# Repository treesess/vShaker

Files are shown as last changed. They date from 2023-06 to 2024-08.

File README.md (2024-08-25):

# vShaker

low-cost shake table and demonstrative test models based on Klipper and FDM mainly for educational purposes

Please refer to the latest folder v231111. Currently there is no full build version to share but only the linear module part has been sorted and uploaded with BOM and installation steps. For the whole build, only some pictures and descriptions fyi [here](https://github.com/treesess/vShaker/blob/main/v231111/CAD/readme.md) 



The vShaker project included the models mainly made from FDM. By using color markers and a normal telephoto DSLR camera or video taker and some basic coding, you can easily get the displacement of all floors. The stiffness and mass are easy to measure. Damping ratio of the model can be calculated from free vibration data. 

There is an example of the free vibration displacement of the model: 



The model was designed to be modular, therefor the mass of each floor can be changed at will. More complicated damper, bracings can be added as well. 

|			|									|
|---			|---									|				
|Floor dimension LxW  | 100x100 mm |
|Floor height      |90 mm  |
|Slab thickness    |11 mm  |
|Column cross section dimension  |1.3x10.8 mm|
|Mass of each floor (m)  |61.75 grams|
|Stiffness of first floor (k1)  |113.98 N/m|
|Stiffness of other floors (k2)  |  116.64 N/m|
|Theoratical natural frequency in Hz  |   1.9608;    5.7274;    9.0386;   11.6250;   13.2706|
|Natural frequency calculated from free vibration measured displacement by FFT in Hz|2.068|

Damping ratio of each floor (ξ) calculated from free vibration displacement:

|			|									|
|---			|---									|		
|1f|0.0379|
|2f|0.0378|
|3f|0.0340|
|4f|0.0222|
|5f|0.0161|



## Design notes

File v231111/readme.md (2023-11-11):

This is my current working version. 

Calling it a shake table is not actually so true, i'd rather say it is just a linear motion design or something like that. 

## BOM

To assemble one of this linear motion module, you will need the below stuff except for the printed parts: 

|Item No.	|Item Description								|Qty.	|
|---		|---											|---	|
|1			|2020 aluminum extrusion, 340 mm in my case.	|1		|
|2			|42 stepping motors, 4260/4248 in my cases.		|2		|
|3			|linear rail, MGN9h	with **TWO** sliders		|1		|
|4			|GT2 Open Belt 6 mm								|depend how long of your Item 1 is.	|
|5			|M3x8 BHCS										|~20	|
|6			|M5x10 BHCS										|8		|
|7			|M5 T-nut										|8		|

hope i didn't miss anything in the table...

Here are the photos for your reference: 



**Figure 1** Assembled module



**Figure 2** Assembled details

## Assemble tips



**Figure 3** Ready up rail and printed carriage



**Figure 4** Push belt into printed carriage like this

You may need to try by yourself to estimate the length of belt you need. I believe you can do that without any tips. A bit longer or shorter won't be a problem since you can see there are huge margin left in the carriage. 



**Figure 5** Use guiding tools to align the linear rail when install it onto 2020 extrusion

After installing the linear rail onto the 2020 extrusion, mount the 42 motor with printed casing by 4 M3x8 BHCS, then embed four of M5 T-nuts in the slots of 2020 extrusion and finish the installation of the motors at both ends of the extrusion. 

**Please be careful checkout the relative direction of carriage and motor casing. They should be like the below photo.**



**Figure 6** Installation of motor

And the pulley of course. Since i used printed 40 teeth pulley, M3 screw and M3 nut were needed in order to fasten the pulley on the shaft of motor. 

By now you should be able to confirm the length of belt you need. 

## Misc. 

Whatever you want to install on the carriage, it will be fixed by M3 screws. the length of those M3 screws will be decided by the stuff you load on the carriage. 

For example, i mounted 6 mm thick PMMA plate CNC with holes, M3x16 screws (if memory serves, sorry) were used. Those screws will directly screw into the sliders on linear rail.

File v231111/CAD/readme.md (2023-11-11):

Except for the design of motion part, actually a whole shake table was made. However, due to the deadline of using it, it used too many weird parts and recycled materials, thus i don't think you really need the CAD for that. Perhaps later on i can make a more universal version of the whole shake table. 

By saying this, i simply want to express that it can work well (but just not ready for everyone to print yet). 

And i believe the provided CAD and STL is enough for you to build your shake table with your style of electronic compartment and a solid base. 



**Figure 1** my rush design of vShaker



**Figure 2** i think you don't want this weird electronic compartment and supporting legs



**Figure 3** and the back of skirt is rough... (and you really don't need that 500 W ACDC) 



**Figure 4** anyway, i tried to make it look good

Yes, it's VORON style.



**Figure 5** After completion only one power supply cord is needed, yes, VORON part here

WIFI control is a must for this one. Only one button: the power on/off. 

----

Basically this is the end of story. No photo taken for the lower part of skirt.

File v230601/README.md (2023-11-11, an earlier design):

# vShaker

low cost shake table and demostrative test models based on Klipper and FDM mainly for educational purposes. 

**This is the old version of the design. Please go to the newer folder. Thanks.**



## intro

This is a lightweight, low cost, educational demonstrative shaker table project with test models. 

The goal here is to use the basis of DIY 3D printer construction to make a simulation of ground seismic motion. Being a lover of FDM printers (especially Voron), this is my best idea to realize the function. 

All you need is some standard aluminum extrusions as frames, linear rails, M3 screw bolts and heat inserts for fastening, 2GT belts, stepper motors, pulleys, and an FDM printer to print the plastic parts. Yes since it is plastic-based, the potential must be great. Hope more people could join in the designing of test models and make the vibration visualized for the students and have fun for the enthusiasts. 

• You may check on the Gallery and demo video here https://youtu.be/Q72j9hyX5CE to see if this is something you do want. 

• If you want it check on the BOM folder for the list of materials

• You will need a 3D printer to print the parts in STL folder. I tried my best to make all parts easy to print. But be careful about tolerance. Check out the pdf for details. 

• If you need further info, check out CAD folder for the original Fusion360 models. Forgive me I'm a not a skillful designer and the timeline may look a bit messy. 

I'd say again that I'm only an amateur doing mechanical design thus the design of the shaker/shaking table may have some issues. Hope some professionals could share an optimized design. 

## keywords about this project
seismic demo

earthquake demonstration

shake table

shake table experiments

shaker

ground motion

educational demonstration

educational display

vibration mechanics

mechanics of vibration

resonance

civil engineering

Klipper

stepper motor

linear modules

FDM

3D printing

vase mode printing

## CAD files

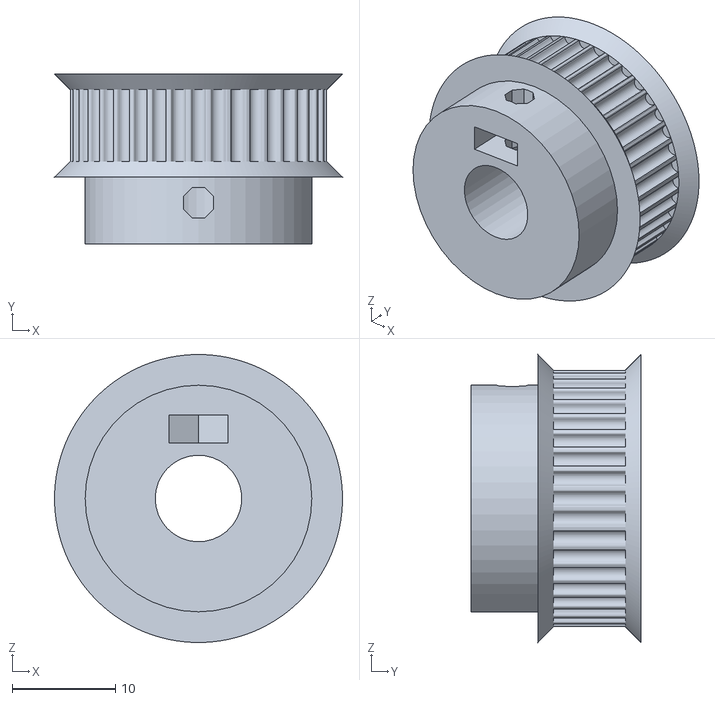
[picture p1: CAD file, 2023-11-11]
v231111/STL/pulley40t.stl
28.0 x 16.5 x 28.0

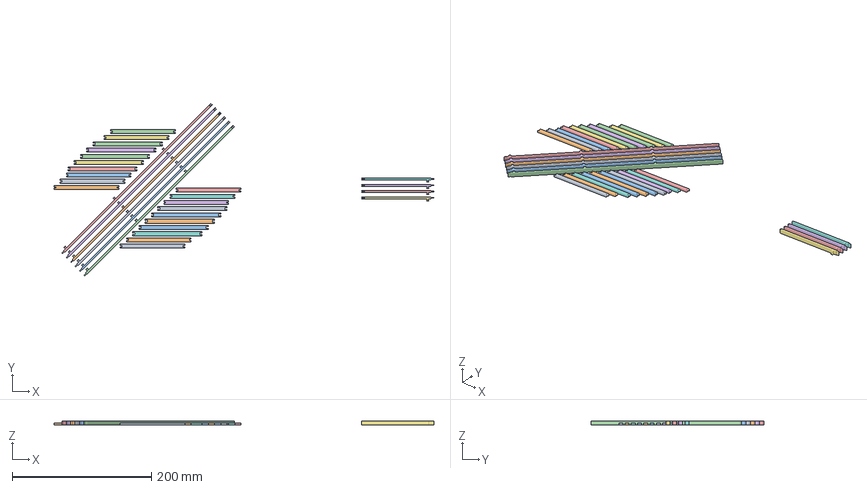
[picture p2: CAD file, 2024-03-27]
v240327 test model (for vShaker compe)/col x beams_slim slice.3mf
546.4 x 248.3 x 6.00 mm
xbeam.stl
ybeam.stl
column.stl
column 3 storey x1.stl

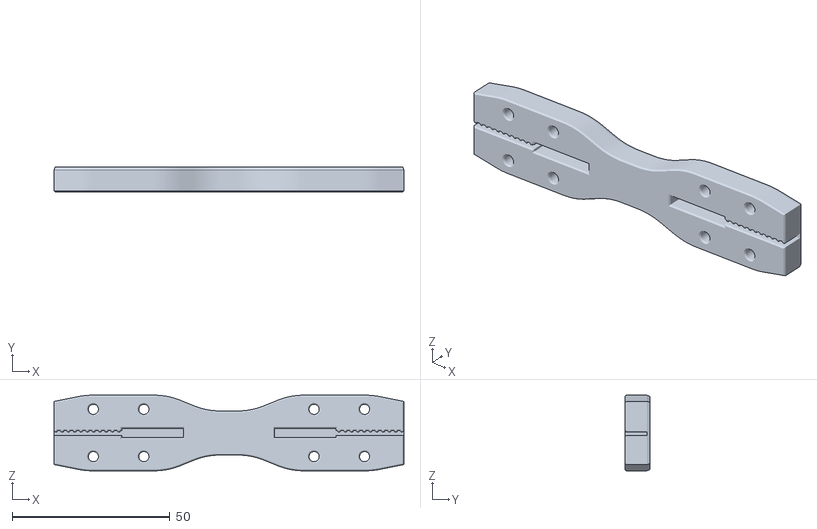
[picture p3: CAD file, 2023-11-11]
v231111/STL/carriage bent belt style - dual slider.stl
111.0 x 8.00 x 24.0

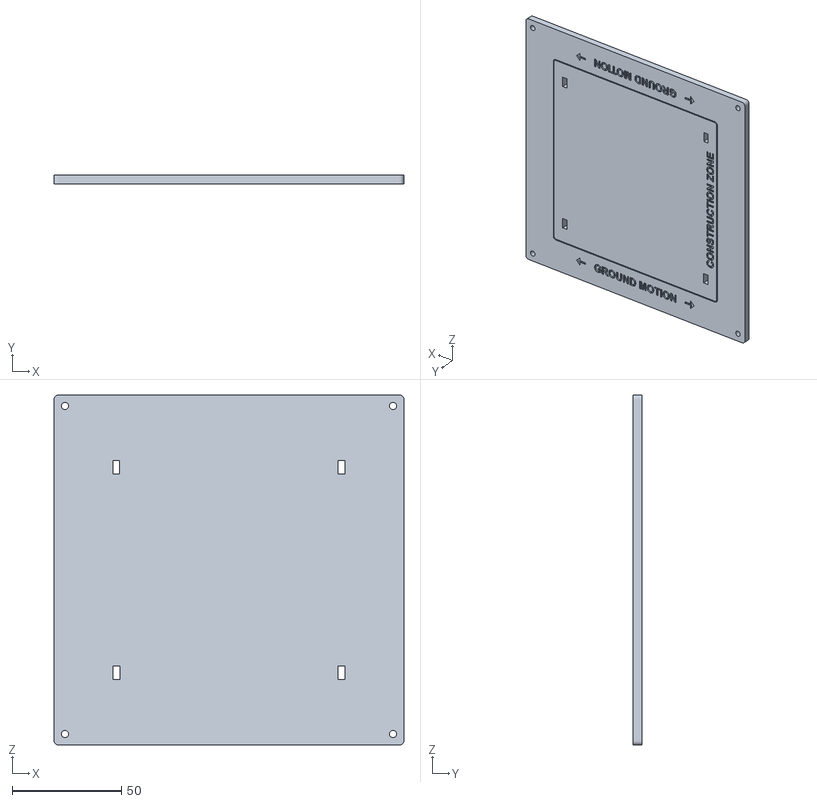
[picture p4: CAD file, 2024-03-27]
v240327 test model (for vShaker compe)/BUILD PLATE 230719 taster temp.stl
160.0 x 4.00 x 160.0

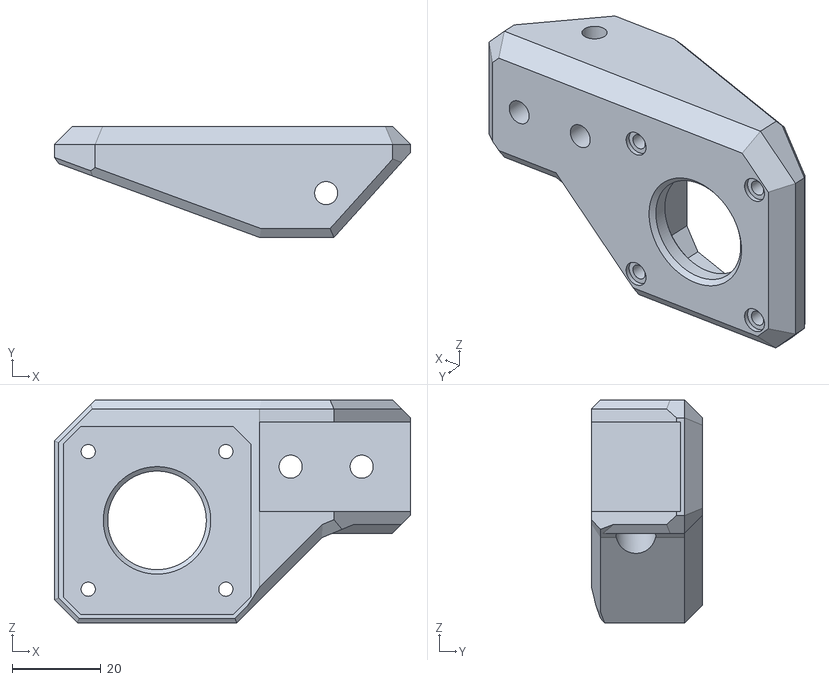
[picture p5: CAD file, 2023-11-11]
v231111/STL/motor casing for 40tpulley.stl
80.2 x 25.0 x 50.2

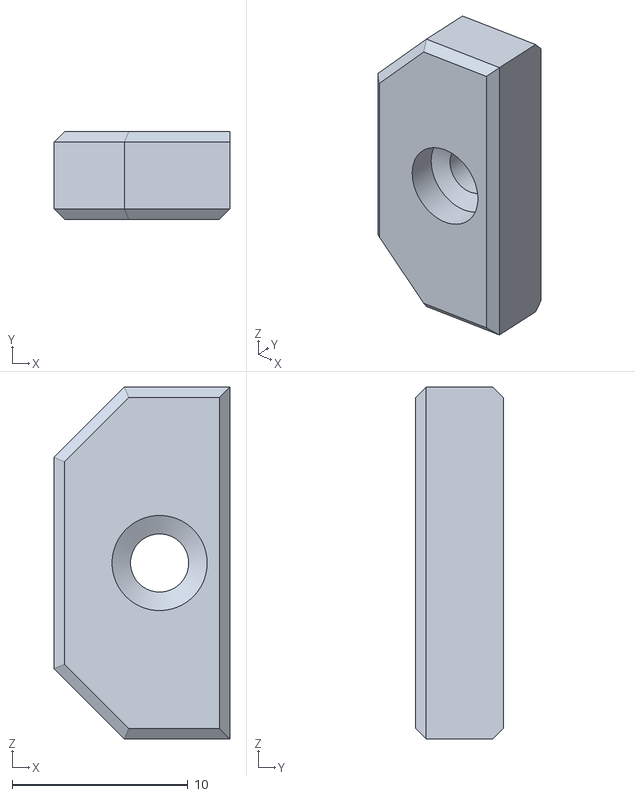
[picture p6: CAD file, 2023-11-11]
v231111/STL/slider stopper.stl
10.0 x 5.00 x 20.0

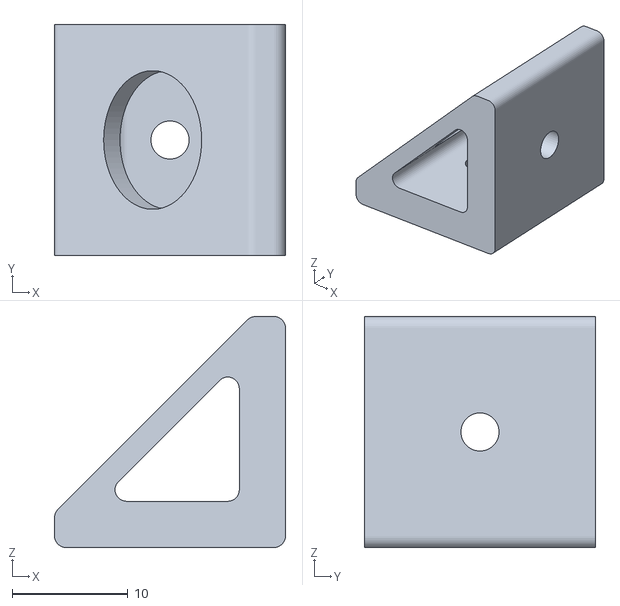
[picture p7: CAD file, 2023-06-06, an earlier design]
v230601/STL/A shake table/2020 extrusion cross connector.stl
20.0 x 20.0 x 20.0

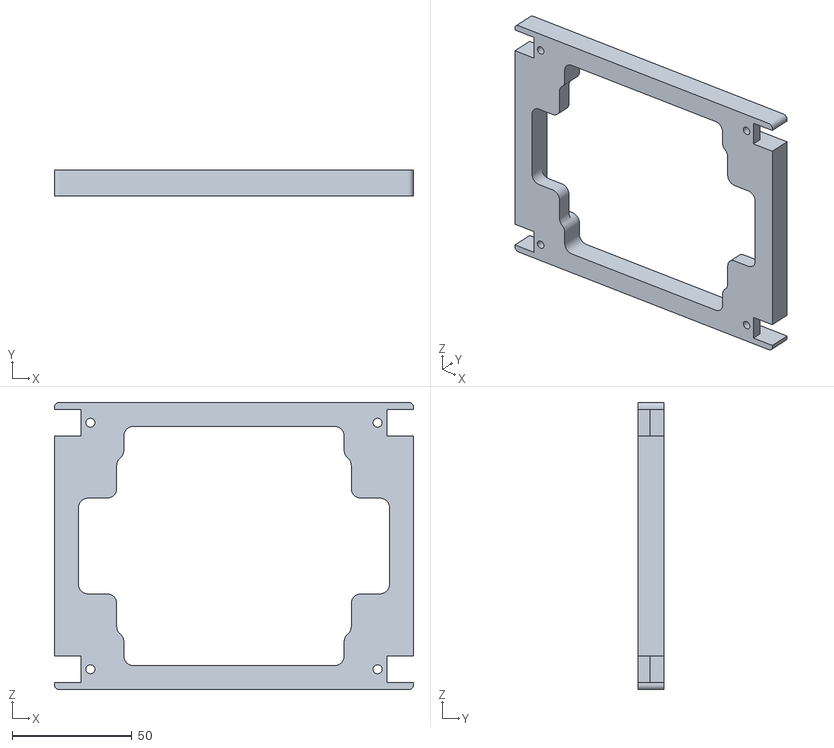
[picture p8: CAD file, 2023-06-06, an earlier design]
v230601/STL/B test model - five storey building/slab - hollow.stl
150.0 x 11.0 x 120.0

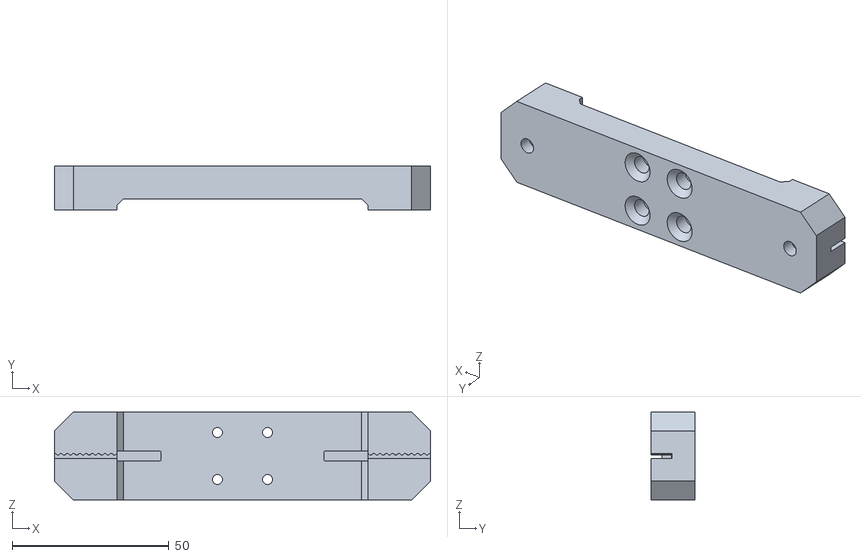
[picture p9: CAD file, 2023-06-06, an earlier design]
v230601/STL/A shake table/linear rail mounting.stl
120.0 x 14.0 x 28.0

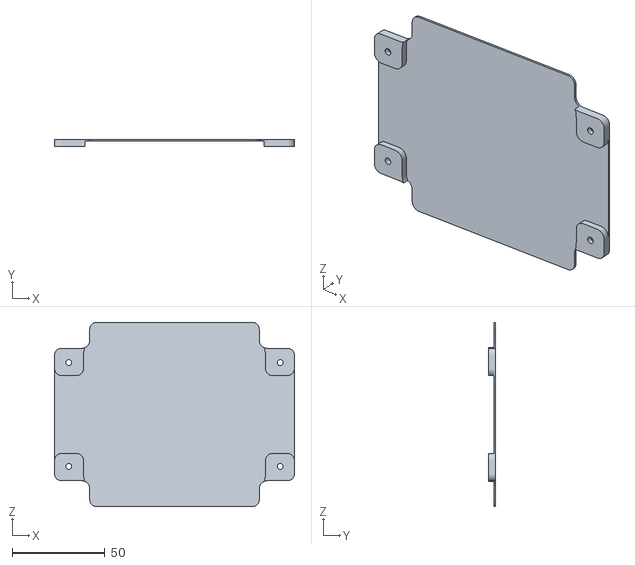
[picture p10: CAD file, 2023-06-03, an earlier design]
v230601/STL/B test model - five storey building/slab cover - -0.3 mm pushed back.stl
129.4 x 4.00 x 99.4

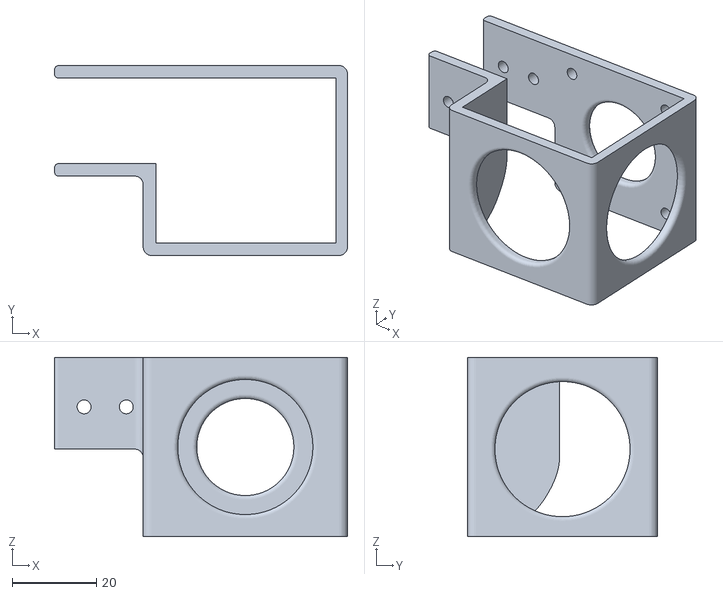
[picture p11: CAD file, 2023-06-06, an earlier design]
v230601/STL/A shake table/motor mounting.stl
69.4 x 45.0 x 42.4

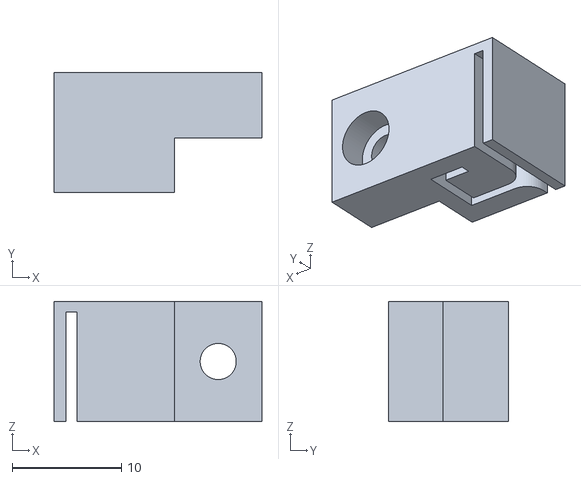
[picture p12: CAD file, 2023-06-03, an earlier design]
v230601/STL/B test model - five storey building/column to slab joint 2.stl
19.0 x 11.0 x 11.0

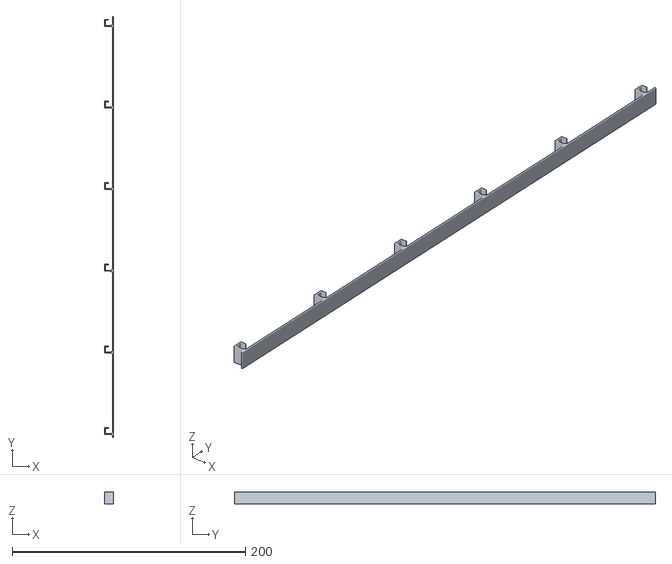
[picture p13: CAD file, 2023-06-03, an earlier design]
v230601/STL/B test model - five storey building/column - preferrable printed in vase mode.stl
7.80 x 361.0 x 10.0

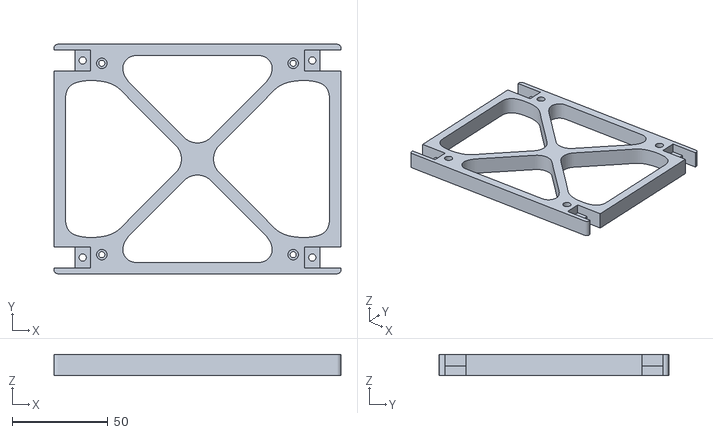
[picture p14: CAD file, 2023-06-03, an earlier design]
v230601/STL/B test model - five storey building/ground slab.stl
150.0 x 120.0 x 11.0

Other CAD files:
v231111/STL/motor casing for 40tpulley - mirror.stl
v230601/STL/A shake table/motor mounting - mirror.stl
v230601/STL/B test model - five storey building/column to slab joint 1.stl
v230601/STL/B test model - five storey building/slab.stl
v230601/CAD/A shake table - 2020 extrusion cross connector.f3d
v230601/CAD/A shake table - motor mounting.f3d
v230601/CAD/A shake table - slider mounting.f3d
v231111/CAD/231011 vShaker, dual slider, pulley40T v20.f3d
v240327 test model (for vShaker compe)/230714 vShaker test model, compe, slab centered v15.f3d

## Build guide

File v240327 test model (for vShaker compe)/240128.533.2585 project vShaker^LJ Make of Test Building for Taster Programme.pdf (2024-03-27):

240128.533.2585 project vShaker, Taster Programme, Earthquake competition

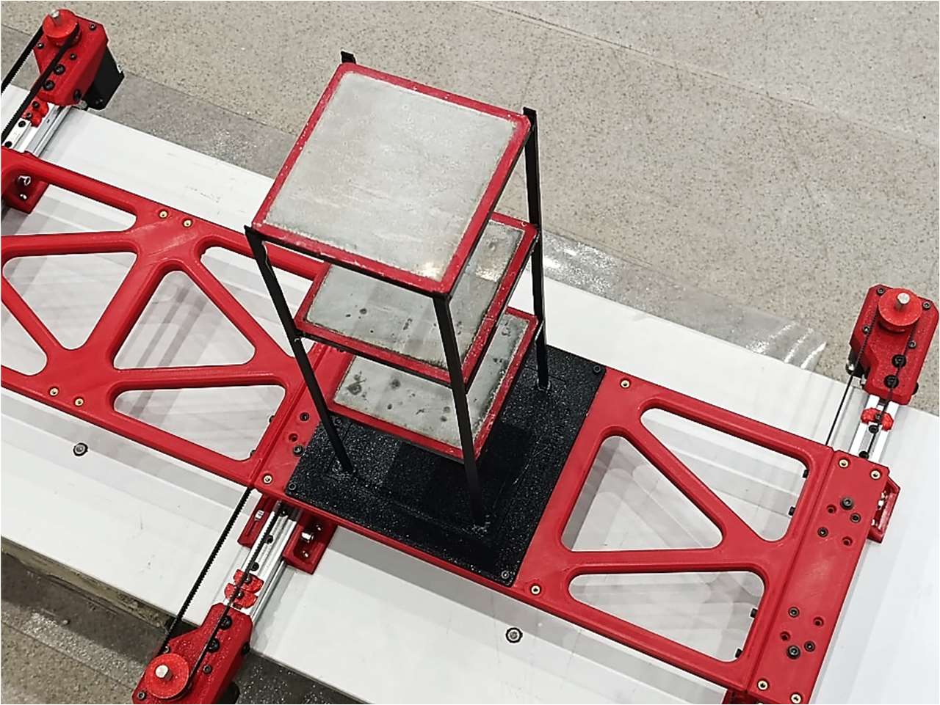
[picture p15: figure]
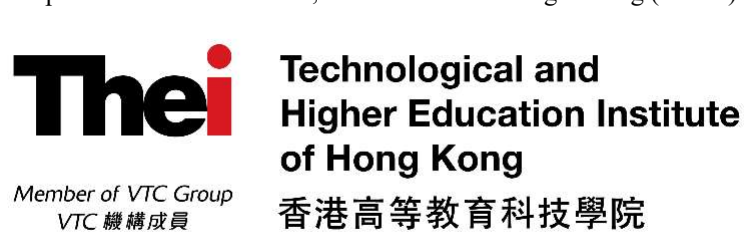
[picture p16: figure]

Page 1 of 6

Introduction of taster programme Earthquake Competition (抗震大激戰)

From here let’s start to build your miniature building, using the 3D printed elements and precast slabs (representing the basic structural column, beams and concrete slabs). Then get it reinforced by your creativity and see how it go through a simulated earthquake!
Have fun!

By Civil Engineering Programme Department of Construction, Environment and Engineering (DCEE)

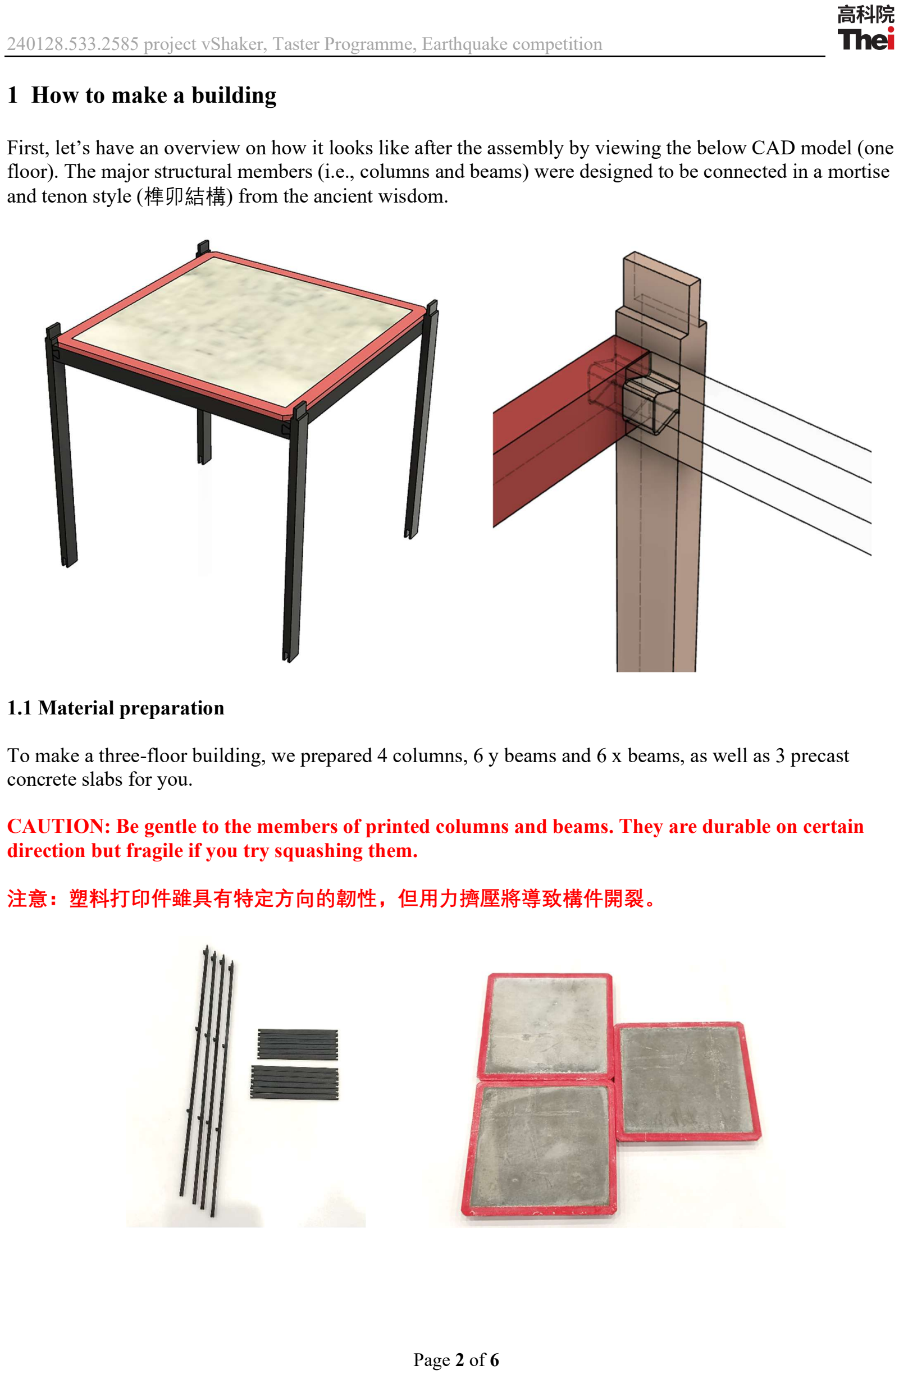
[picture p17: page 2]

Page 2 of 6

### 1 How to make a building

First, let’s have an overview on how it looks like after the assembly by viewing the below CAD model (one floor). The major structural members (i.e., columns and beams) were designed to be connected in a mortise and tenon style (榫卯結構) from the ancient wisdom.

### 1.1 Material preparation

To make a three-floor building, we prepared 4 columns, 6 y beams and 6 x beams, as well as 3 precast concrete slabs for you.

CAUTION: Be gentle to the members of printed columns and beams. They are durable on certain direction but fragile if you try squashing them.

注意：塑料打印件雖具有特定方向的韌性，但用力擠壓將導致構件開裂。

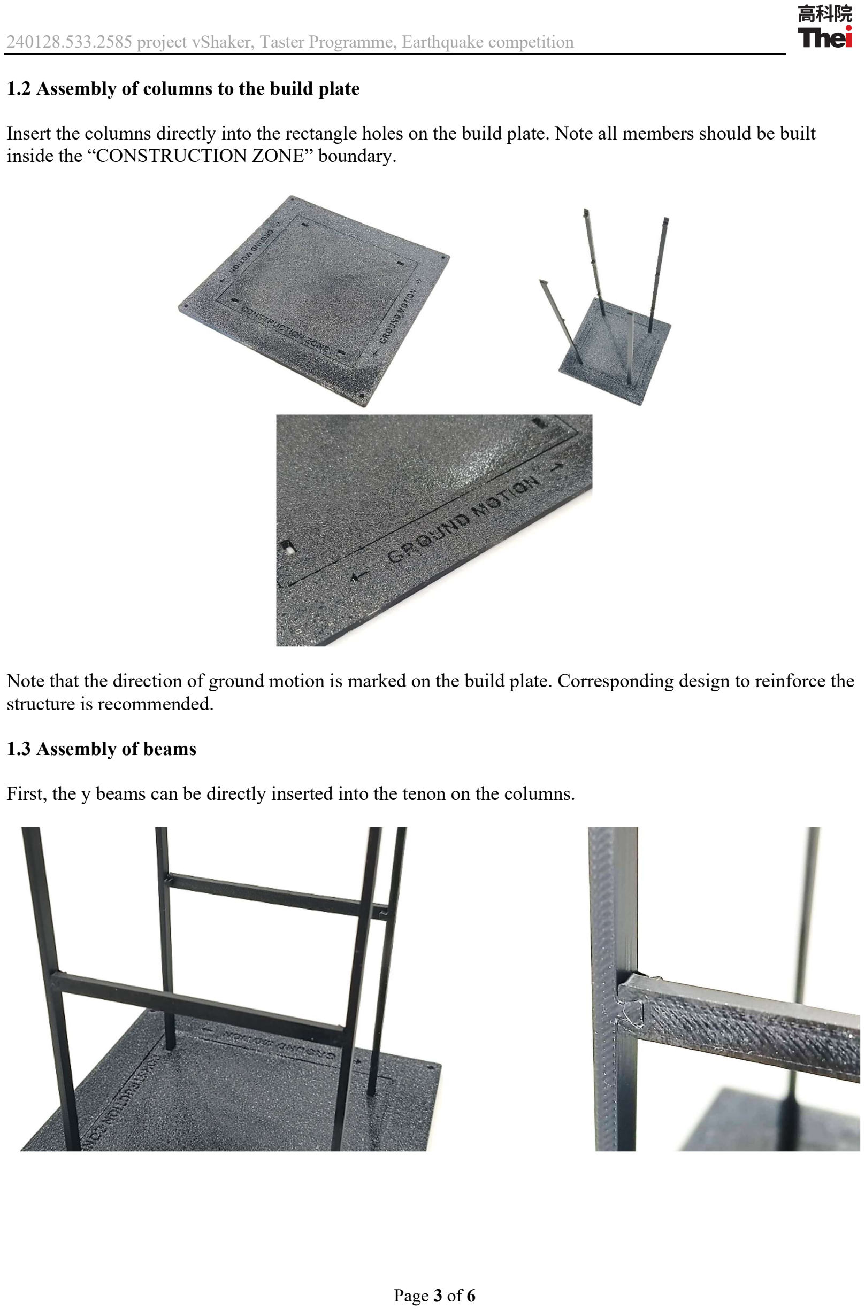
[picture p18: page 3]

Page 3 of 6

### 1.2 Assembly of columns to the build plate

Insert the columns directly into the rectangle holes on the build plate. Note all members should be built inside the “CONSTRUCTION ZONE” boundary.

Note that the direction of ground motion is marked on the build plate. Corresponding design to reinforce the structure is recommended.

### 1.3 Assembly of beams

First, the y beams can be directly inserted into the tenon on the columns.

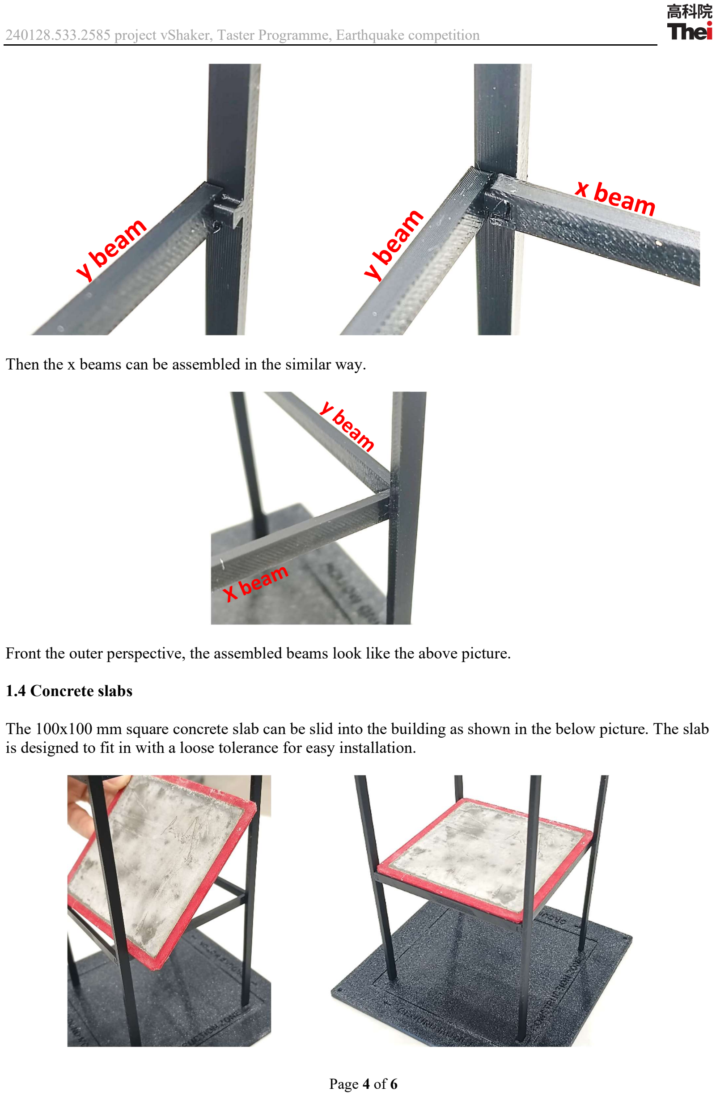
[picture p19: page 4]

Page 4 of 6

Then the x beams can be assembled in the similar way.

Front the outer perspective, the assembled beams look like the above picture.

### 1.4 Concrete slabs

The 100x100 mm square concrete slab can be slid into the building as shown in the below picture. The slab is designed to fit in with a loose tolerance for easy installation.

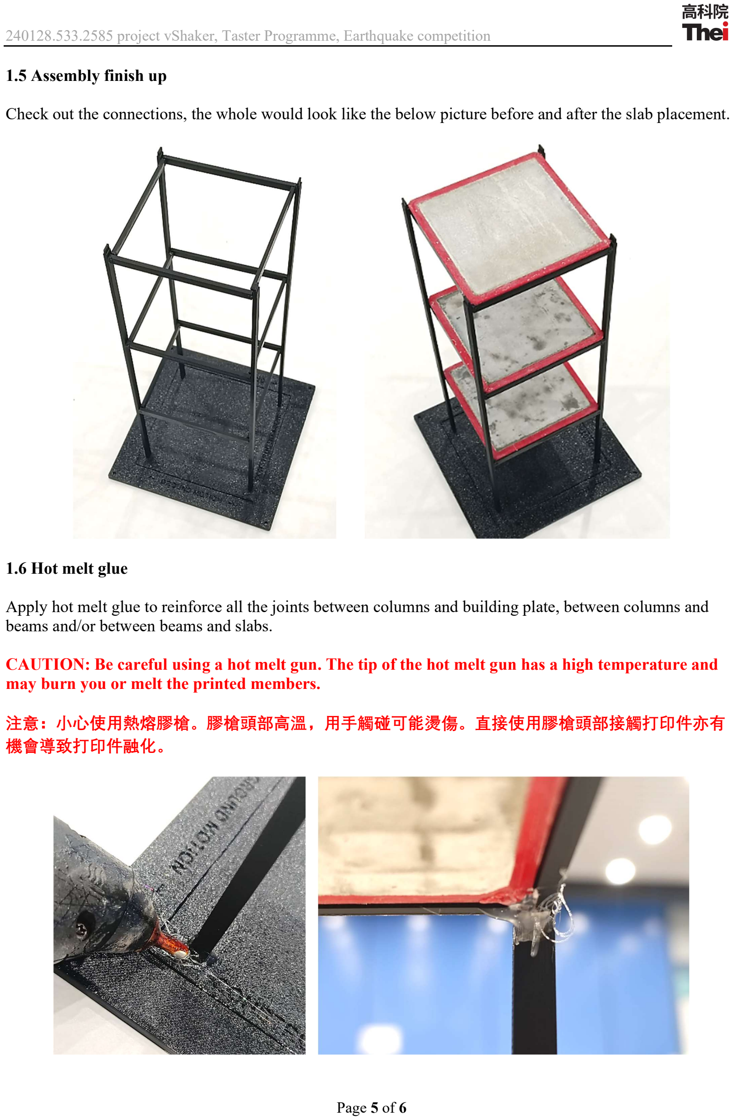
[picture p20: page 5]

Page 5 of 6

### 1.5 Assembly finish up

Check out the connections, the whole would look like the below picture before and after the slab placement.

### 1.6 Hot melt glue

Apply hot melt glue to reinforce all the joints between columns and building plate, between columns and beams and/or between beams and slabs.

CAUTION: Be careful using a hot melt gun. The tip of the hot melt gun has a high temperature and may burn you or melt the printed members.

注意：小心使用熱熔膠槍。膠槍頭部高溫，用手觸碰可能燙傷。直接使用膠槍頭部接觸打印件亦有 機會導致打印件融化。

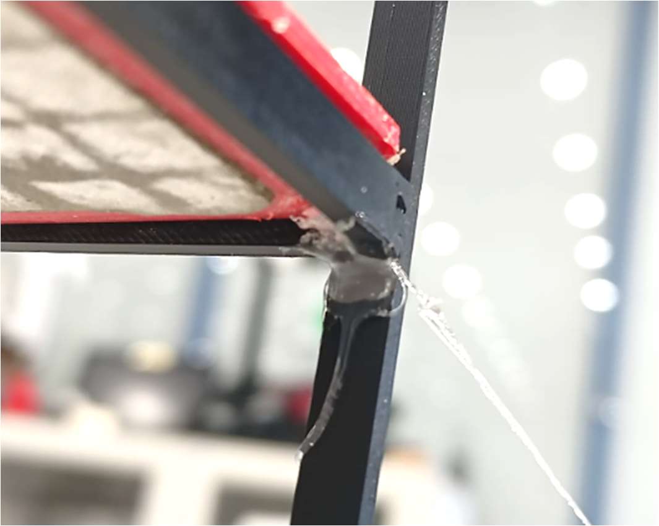
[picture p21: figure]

Page 6 of 6

Clean up the excessive hot melt glue to make it look better.

Congrats! Now you have finished the basic build and ready to use your creativity to do the reinforcement and make this building stand strong in an earthquake!

*1.7 (Optional) Building the fourth floor

If you want to challenge the sky, we provide extra materials for you to build the forth floor! Make it and get higher score!

### 2 Earthquake competition basic rules

All game has rules to make it fair and more interesting!

Here are the basic rules of our game:

a) Game over if any of your slabs drop during the earthquake test.
b) Game over if your building has torsion too large to hit the adjacent building(s). Therefore, try your best to make your building symmetric.
c) Of course, any tools including ruler, scissors, etc., cannot be put in the building as supports.

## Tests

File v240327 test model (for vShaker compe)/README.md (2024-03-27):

## intro

This is the test model info and materials for taster programmes held for young students to play with. N

Note that this is just for short gameplay (excluding the speech and talks, only 1 hour of actual gameplay) without extra preparation for the young participants. So the purpose is for fun for the youngsters therefor might not look so pretty made by the students. i would say the potential of this design is large lol. 

----

Students making the model for this short taster game:



Ready to shake and see which team would win: 



gameplay result of one of our tasters: 



CAD view of the model for this short taster game: 



The design is as modular as possible. You can easily adjust the parameters in the .f3d file. 

## vShaker compe

first off, this is the completed vShaker compe machine i made: 









suggest using 4060 stepper motors or even more powerful ones if you are going to do heavy game play. 



I tucked the whole electronic part under the shake table. Note that the temperature would be too high if you don't have enough cooling. 

a random build of a model with A4 paper as reinforcement on the shake table for preliminary test. 



## How to print and make the model

For print parameters please check the .3mf file for reference. 

Suggest using PLA matt to print, which would be not too strong and not too weak, to achieve the game purpose. 



Suggest using flat bed but not PEI plate for better consistency of the column beam elements. 

Suggest using cement paste for the casting of slabs with water cement ratio (w/c) between 0.3 to 0.4 for the balance of workability and strength. 

Suggest fixing the slab frame with texture tape and hot melt glue before casting. The below photo used using glass plate as the bottom plate, but lately i found that using thin wood plate or flexible plastic plate as the bottom would be much easier to compaction when casting and easier to demold. 



If failed to vibrate enough after casting, the quality and appearance of the slabs might be bad: 



Suggest using ABS but not PLA to print the slab frame since PLA will do bad with water. i used eSUN PLA+ in the beginning, looked okay but not durable enough. so i started to switch to ABS prints. 

## misc. 

Please refer to the PDF manual for building the how of building the model to play the game.
